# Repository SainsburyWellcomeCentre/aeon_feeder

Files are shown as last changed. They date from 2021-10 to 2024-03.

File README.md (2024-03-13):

# Aeon Feeder
Complete project repository for the underground feeder used in project Aeon.
## Folder Structure
### Code
This folder contains the VS Code project and code for the Raspberry Pi Pico
### eCAD
This folder contains 2 Altium Designer project folders for the Application Board and Beam Brake.

Within each project folder all the design files as well as another folder called __Project Outputs__

The __Project Outputs__ folder contains files for Documentation, Assembly and Fabrication.
### mCAD
This folder contains the complete mechanical design in Inventor 2023 project format.

To use this project within Inventor 2023+, the user should first open the Inventor Project file called **AEON.Feeder.ipj**

This will ensure Inventor is using the correct Project file to correctly find and assemble the the parts and assemblies within the Feeder.

The project can be opened from any location where the user has chosen to pull the whole project.

The main assembly for the complete model is **AEON.Feeder._Main.iam**

## Notes
The required software for the project is as follows
* Microsoft Visual Studio and Raspberry Pi Pico SDK as setup within the [Getting Started with Pico](https://datasheets.raspberrypi.com/pico/getting-started-with-pico.pdf)
* Altium Designer 23.5 or newer. Academic licenses can be obtained by contacting [Altium Education](https://www.altium.com/education/)
* Inventor Pro 2023 or newer. Academic licenses can be obtained by contacting [Autodesk Education](https://www.autodesk.com/education/home)

## Citation Policy

If you use this software or hardware, please cite it as below:

Sainsbury Wellcome Centre Foraging Behaviour Working Group. (2023). Aeon: An open-source platform to study the neural basis of ethological behaviours over naturalistic timescales,  https://doi.org/10.5281/zenodo.8411157



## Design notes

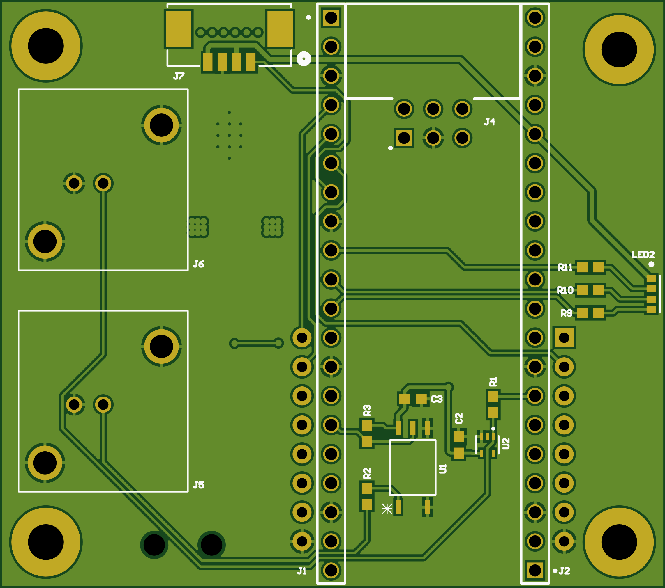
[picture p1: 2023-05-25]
mCAD/AEON.FeederElectronics/G_262400806_TopDecalImage.png

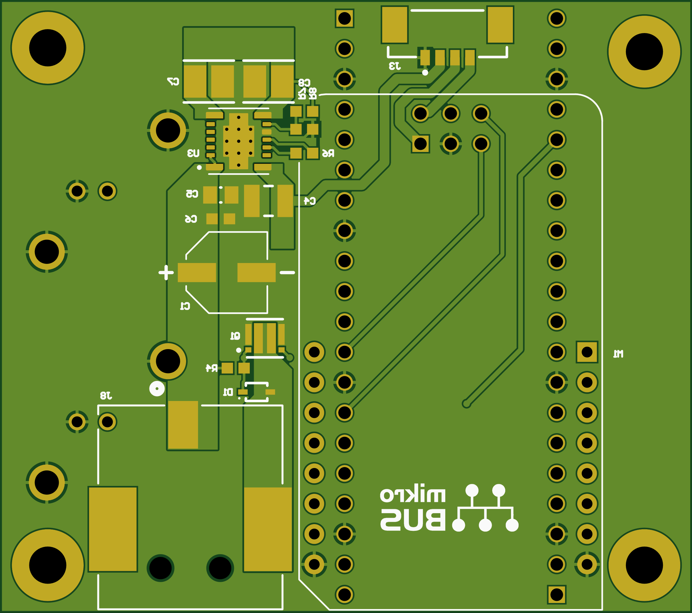
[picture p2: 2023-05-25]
mCAD/AEON.FeederElectronics/G_262400806_BottomDecalImage.png

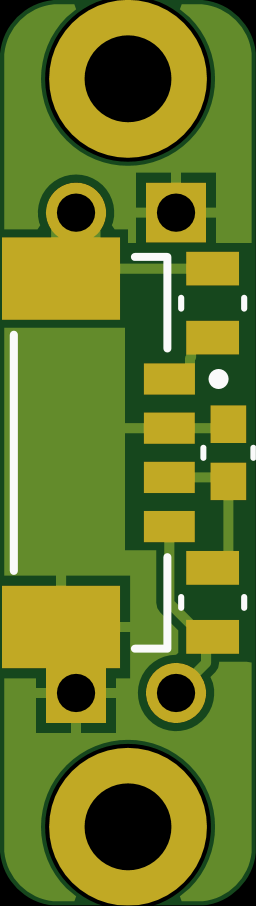
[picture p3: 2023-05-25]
mCAD/AEON.Feeder.BeamBreak/G_-1522103576_TopDecalImage.png

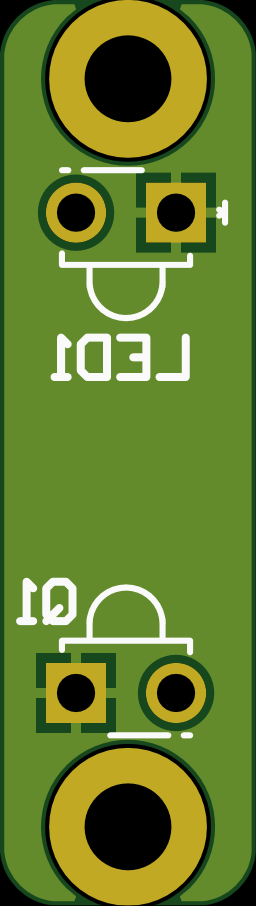
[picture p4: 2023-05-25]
mCAD/AEON.Feeder.BeamBreak/G_-1522103576_BottomDecalImage.png

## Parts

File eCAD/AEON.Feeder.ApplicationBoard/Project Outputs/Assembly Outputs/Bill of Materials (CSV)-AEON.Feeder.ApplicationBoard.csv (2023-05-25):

Comment | Description | Designator | Quantity
CPOLD-10uF-50V-20%-Alu | 10µF ±20% 50V SMD Aluminum Electrolytic Capacitor Surface Mount D | C1 | 1
C0603-100nF-100V-10%-X7R | 0.1µF ±10% 100V Ceramic Capacitor X7R 0603 (1608 Metric) | C2, C3, C6 | 3
C1210-10uF-50V-10%-X7R | 10uF ±10% 50V Ceramic Capacitor X7R 1210 (3225 Metric) | C4 | 1
C0805-1uF-50V-10%-X7R | 1uF ±10% 50V Ceramic Capacitor X7R 0805 (2012 Metric) | C5 | 1
C1210-47uF-10V-10%-X7R | 47uF ±10% 10V Ceramic Capacitor X7R 1210 (3225 Metric) | C7, C8 | 2
MM3Z10VB | DIODE ZENER 10V 200MW SOD323F | D1 | 1
SSW-120-01-x-S | Conn Socket Strip SKT 20 POS 2.54mm Solder ST Thru-Hole | J1 | 1
SSW-120-01-x-S - 21-40 | Conn Socket Strip SKT 20 POS 2.54mm Solder ST Thru-Hole (pins 21 - 40) | J2 | 1
53398-0471 | Board Connector, 4 Contact(s), 1 Row(s), Male, Straight, 0.049 inch Pitch, Surface Mount Terminal, Locking, Natural Insulator, Receptacle | J3 | 1
TST-103-04-x-D-RA | Board Connector, 6 Contact(s), 2 Row(s), Male, Right Angle, Solder Terminal | J4 | 1
1-1337541-0 | TE CONNECTIVITY / GREENPAR 1-1337541-0 RF / Coaxial Connector, BNC Coaxial, Straight Jack, Solder, 50 ohm, Brass | J5, J6 | 2
53261-0471 | MOLEX 1.25mm (.049") Pitch PicoBlade Header, Surface Mount, Right Angle, Lead-free, 4 Circuits | J7 | 1
694108105102 | DC Power Connectors WR-DC PwrJk CtrPnSMT Right Angled W/Peg | J8 | 1
MSL0601RGBU1 | Triple Color LED, Red/green/blue, Milky White | LED2 | 1
MIKROE-2699 | DRV8701 Brushed DC Motor Full-Bridge Gate DC Motor Driver 5 Click Add-On Board | M1 | 1
FDMC8030 | ON SEMICONDUCTOR - FDMC8030 - Dual MOSFET, Dual N Channel, 12 A, 40 V, 0.008 ohm, 10 V, 1.5 V | Q1 | 1
R0603-150R-1/16W-0.1% | Surface Mount Resistor 150 Ohm 1/16 W 0.1% 0603 (1608 Metric) | R1 | 1
R0603-270R-1/16W-0.1% | Surface Mount Resistor 270 Ohm 1/16 W 0.1% 0603 (1608 Metric) | R2 | 1
R0603-360R-1/16W-0.1% | Surface Mount Resistor 360 Ohm 1/16 W 0.1% 0603 (1608 Metric) | R3 | 1
R0603-2k7-1/16W-0.1% | Surface Mount Resistor 2k7 Ohm 1/16 W 0.1% 0603 (1608 Metric) | R4 | 1
R0603-100k-1/16W-0.1% | Surface Mount Resistor 100k Ohm 1/16 W 0.1% 0603 (1608 Metric) | R6 | 1
R0603-10k-1/16W-0.1% | Surface Mount Resistor 10k Ohm 1/16 W 0.1% 0603 (1608 Metric) | R7 | 1
R0603-2k49-1/16W-0.1% | Surface Mount Resistor 2.49k Ohm 1/16 W 0.1% 0603 (1608 Metric) | R8 | 1
R0603-1k5-1/16W-0.1% | Surface Mount Resistor 1k5 Ohm 1/16 W 0.1% 0603 (1608 Metric) | R9 | 1
R0603-560R-1/16W-0.1% | Surface Mount Resistor 560 Ohm 1/16 W 0.1% 0603 (1608 Metric) | R10 | 1
R0603-470R-1/16W-0.1% | Surface Mount Resistor 470 Ohm 1/16 W 0.1% 0603 (1608 Metric) | R11 | 1
TLP2368 | TOSHIBA TLP2368(E(O Digital Output Optocoupler, Open Collector, 1 Channel, SOIC, 5 Pins, 3.75 kV, 20 Mbaud | U1 | 1
TPD3E001DRLR | Low-Capacitance 3-Channel +/-15KV ESD-Protection Array for High-Speed Data Interfaces 5-SOT-5X3 | U2 | 1
TPSM5601R5HRDAR | 60-V input, 1-V to 16-V output, 1.5-A power module in enhanced HotRod™ QFN package 15-B3QFN -40 to 125 | U3 | 1

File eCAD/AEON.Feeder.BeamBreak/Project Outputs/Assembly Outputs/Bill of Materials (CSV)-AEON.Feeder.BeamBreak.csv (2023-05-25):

Comment | Description | Designator | Quantity
C0603-100nF-100V-10%-X7R | 0.1µF ±10% 100V Ceramic Capacitor X7R 0603 (1608 Metric) | C1 | 1
53398-0471 | Board Connector, 4 Contact(s), 1 Row(s), Male, Straight, 0.049 inch Pitch, Surface Mount Terminal, Locking, Natural Insulator, Receptacle | J1 | 1
GL480E00000F | EMITTER IR 950NM 50MA RADIAL | LED1 | 1
PT480FE0000F | SHARP PT480FE0000F PHOTOTRANSISTOR | Q1 | 1
RES 0805 200R 0.1% 125mW | RES 0805 200 Ohm 0.1% 1/8W ±10ppm/°C Thin Film | R1 | 1
R0603-6k8-1/16W-0.1% | Surface Mount Resistor 6.8k Ohm 1/16 W 0.1% 0603 (1608 Metric) | R2 | 1

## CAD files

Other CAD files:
mCAD/AEON.AcrylicTop.ipt
mCAD/AEON.AluminiumFrame.ipt
mCAD/AEON.Feeder.Base.ipt
mCAD/AEON.Feeder.BeamBreak/ConvertedComponents/FP-533980471-MFG_CMP-370-0030-2.ipt
mCAD/AEON.Feeder.BeamBreak/ConvertedComponents/FP-GRM188-0_1-e0_2_0_5-IPC_B_CMP-611-0027-15.ipt
mCAD/AEON.Feeder.BeamBreak/ConvertedComponents/GL480_5.8mm_CMP-520-0009-4.ipt
mCAD/AEON.Feeder.BeamBreak/ConvertedComponents/PT480_5.8_CMP-500-0000-3.ipt
mCAD/AEON.Feeder.BeamBreak/ConvertedComponents/RES_ERA6A_0805_PAN_CMP-633-0035-1.ipt
mCAD/AEON.Feeder.BeamBreak/ConvertedComponents/RES_ERA6A_0805_PAN_CMP-633-0036-1.ipt
mCAD/AEON.Feeder.BeamBreak/ND.ForageFeeder.BeamBreak.iam
mCAD/AEON.Feeder.BeamBreak/ND.ForageFeeder.BeamBreak_BOARD.ipt
mCAD/AEON.Feeder.BeamBreakBlock.ipt
mCAD/AEON.Feeder.BearingSpacer.ipt
mCAD/AEON.Feeder.ClampBlock.ipt
mCAD/AEON.Feeder.ClampUpper.ipt
mCAD/AEON.Feeder.Disc.ipt
mCAD/AEON.Feeder.EncodeMount.ipt
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

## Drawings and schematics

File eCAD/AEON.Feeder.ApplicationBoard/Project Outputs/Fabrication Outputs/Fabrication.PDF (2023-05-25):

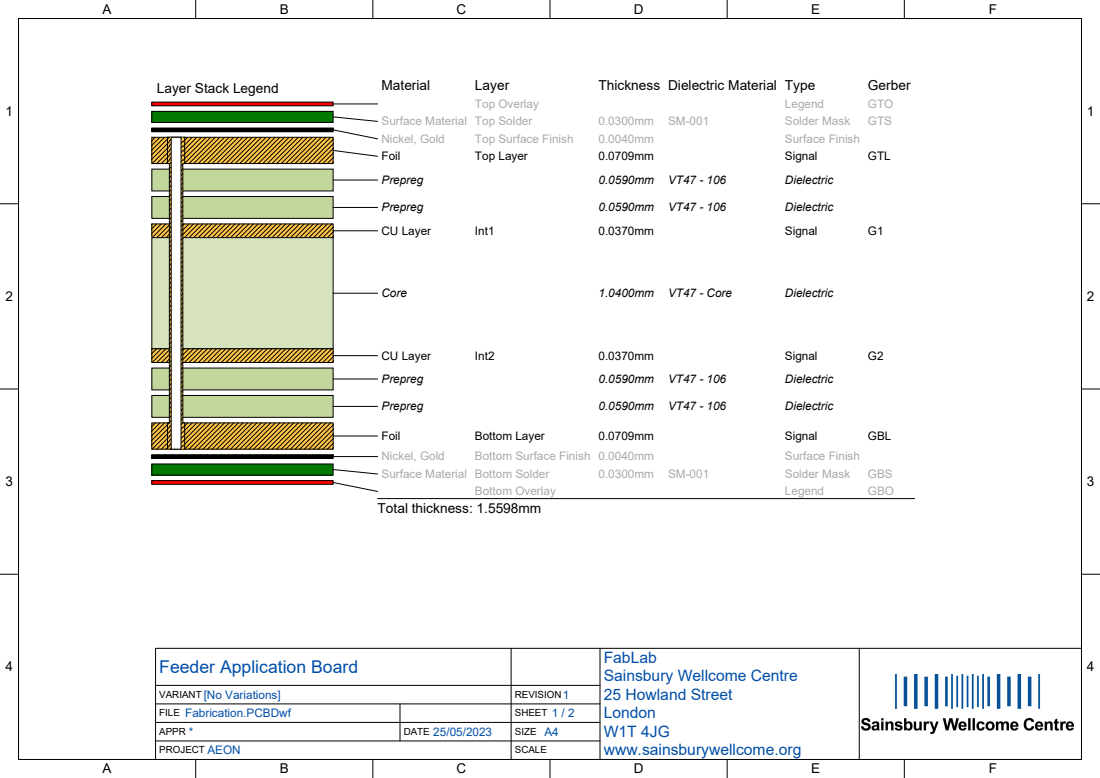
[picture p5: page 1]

[No Variations] VARIANT | 1 REVISION
FILE Fabrication.PCBDwf | | SHEET 1 / 2
APPR * | DATE 25/05/2023 | SIZE A4

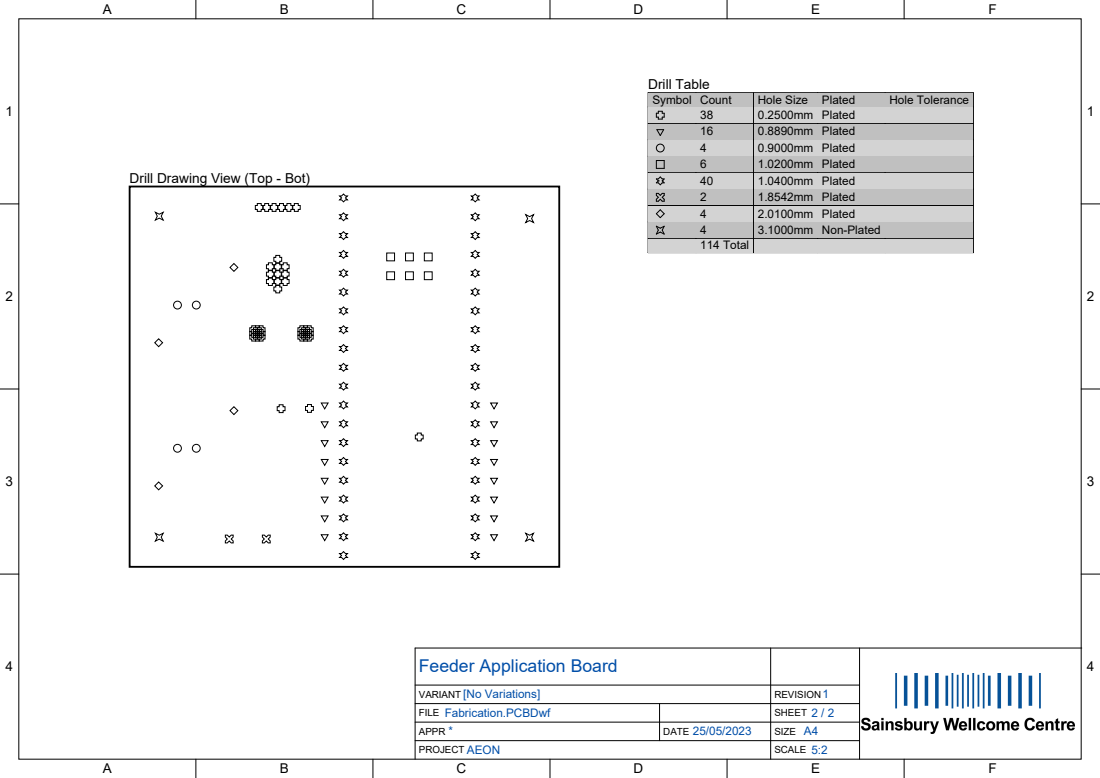
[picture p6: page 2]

Symbol | Count | Hole Size | Plated | Hole Tolerance

38 | 0.2500mm | Plated
16 | 0.8890mm | Plated
4 | 0.9000mm | Plated
6 | 1.0200mm | Plated
40 | 1.0400mm | Plated
2 | 1.8542mm | Plated
4 | 2.0100mm | Plated
4 | 3.1000mm | Non-Plated
114 Total

Drill Drawing View (Top - Bot)

[No Variations] VARIANT | 1 REVISION
FILE Fabrication.PCBDwf | | SHEET 2 / 2
APPR * | DATE 25/05/2023 | SIZE A4

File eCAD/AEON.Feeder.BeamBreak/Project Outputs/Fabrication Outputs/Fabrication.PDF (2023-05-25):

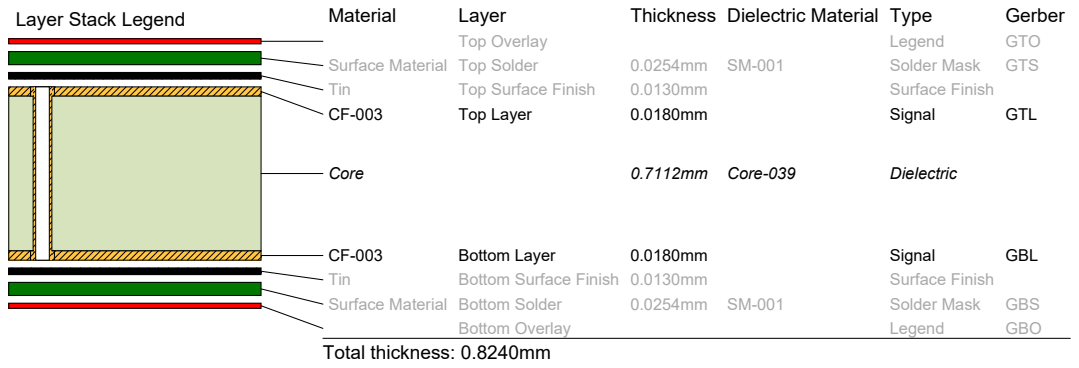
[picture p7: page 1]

[No Variations] VARIANT | 1 REVISION
FILE Fabrication.PCBDwf | | SHEET 1 / 2
APPR * | DATE 25/05/2023 | SIZE A4

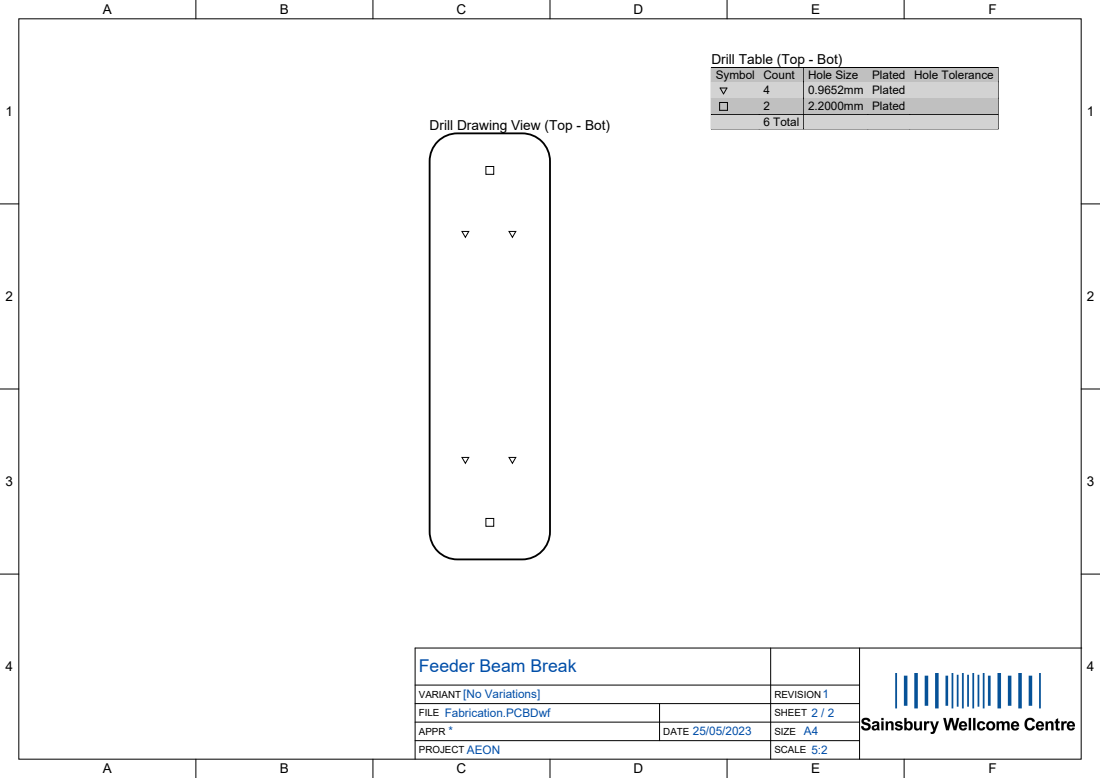
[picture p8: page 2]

Drill Table (Top - Bot)

Symbol | Count | Hole Size | Plated | Hole Tolerance

4 | 0.9652mm | Plated
2 | 2.2000mm | Plated
6 Total

Drill Drawing View (Top - Bot)

[No Variations] VARIANT | 1 REVISION
FILE Fabrication.PCBDwf | | SHEET 2 / 2
APPR * | DATE 25/05/2023 | SIZE A4

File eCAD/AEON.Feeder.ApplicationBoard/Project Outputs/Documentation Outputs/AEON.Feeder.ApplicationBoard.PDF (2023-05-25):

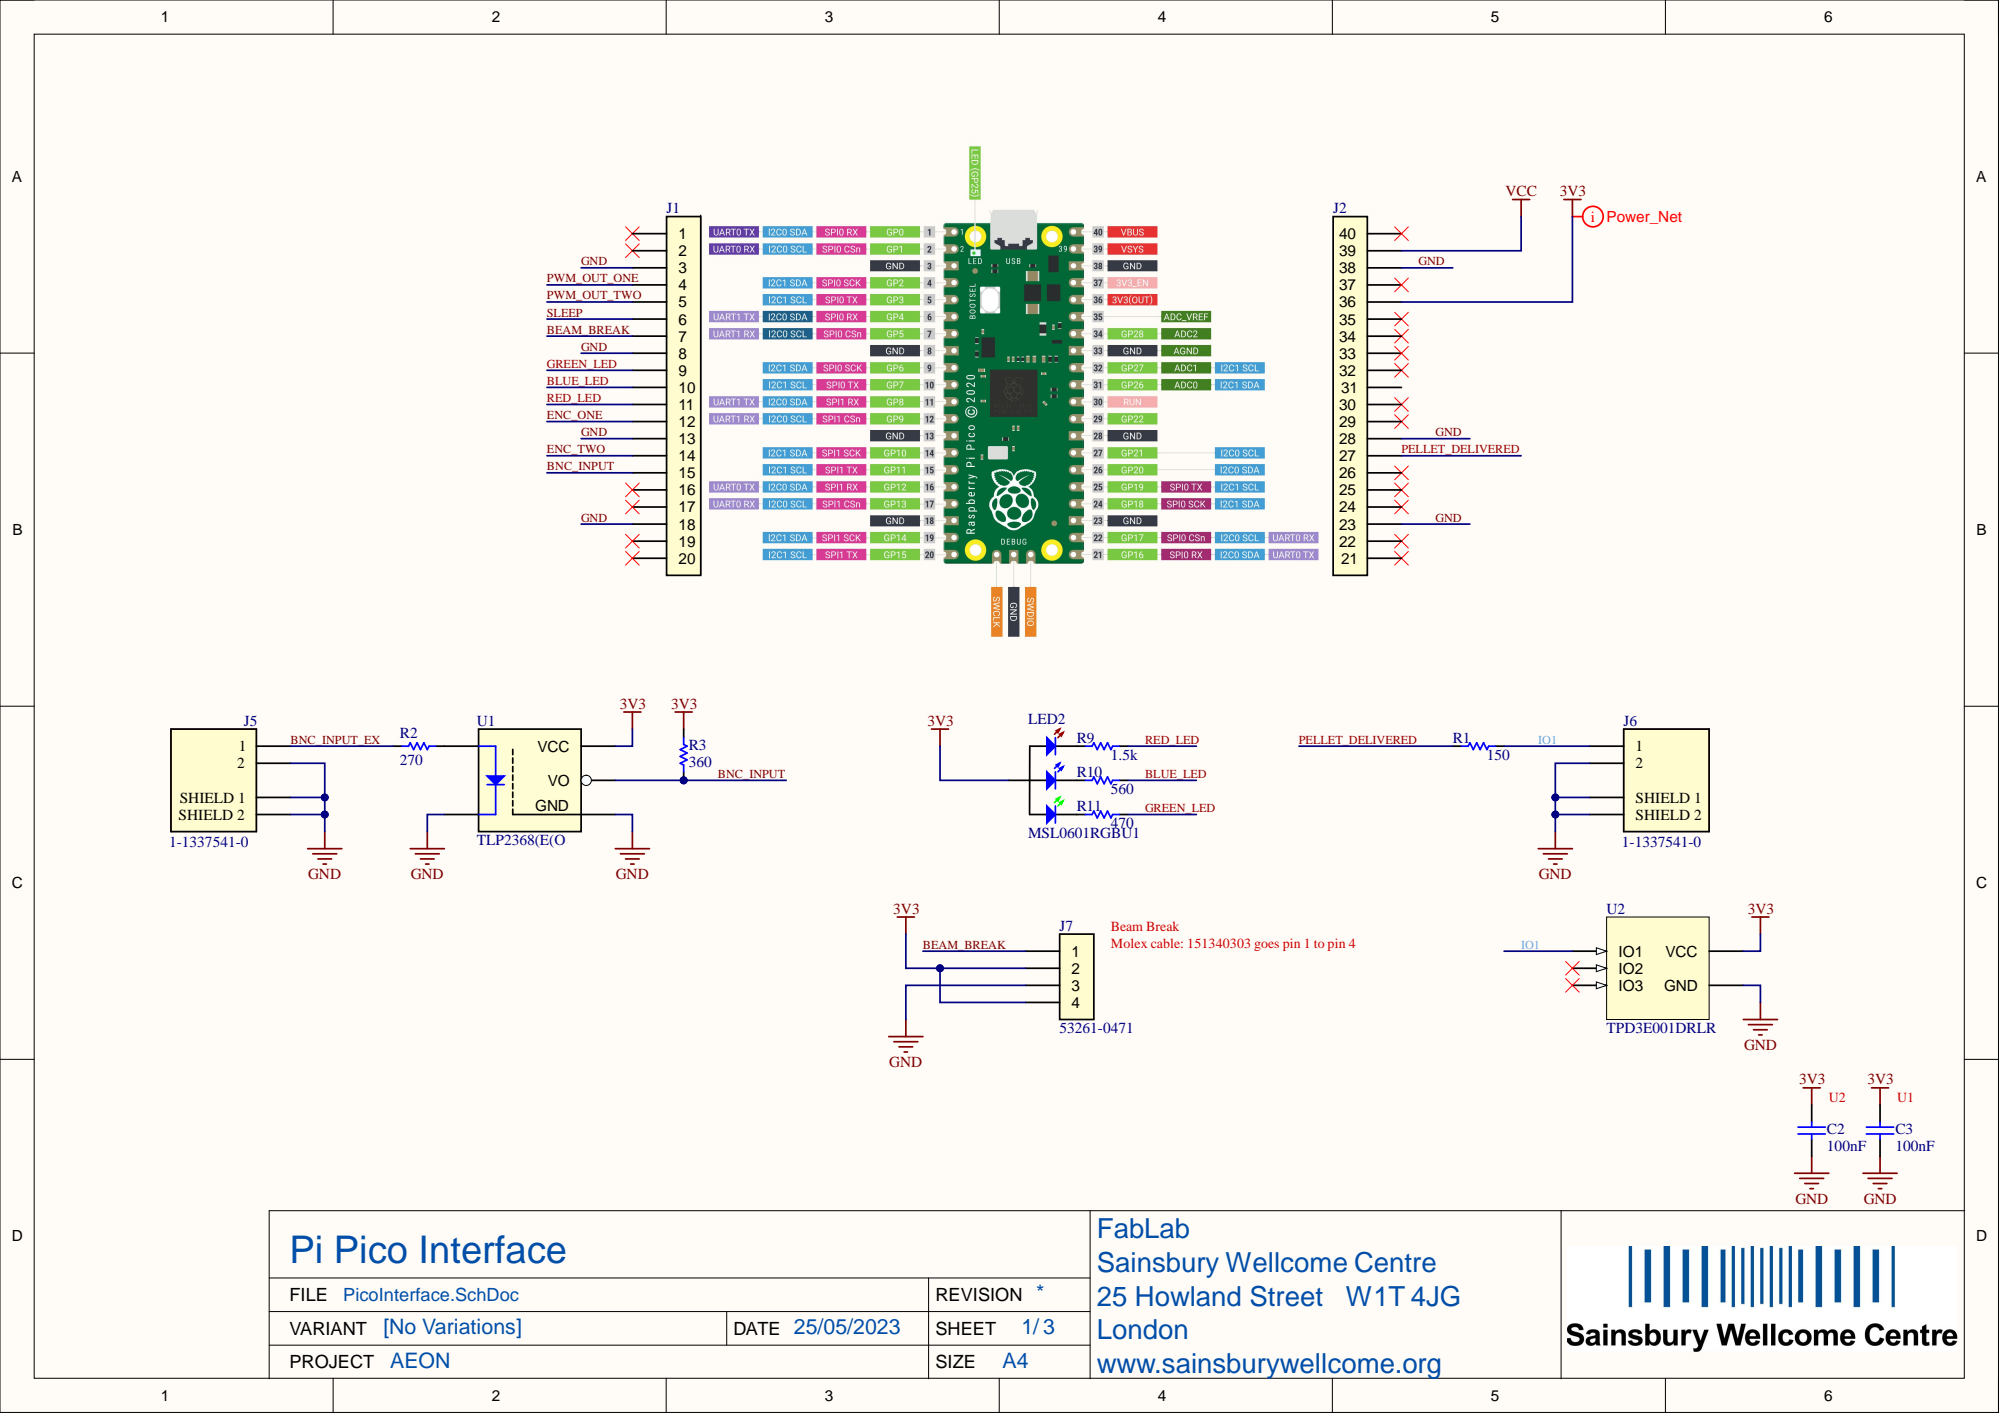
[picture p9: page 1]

Beam Break
Molex cable: 151340303 goes pin 1 to pin 4

FILE PicoInterface.SchDoc | * REVISION

VARIANT [No Variations] | DATE | SHEET /

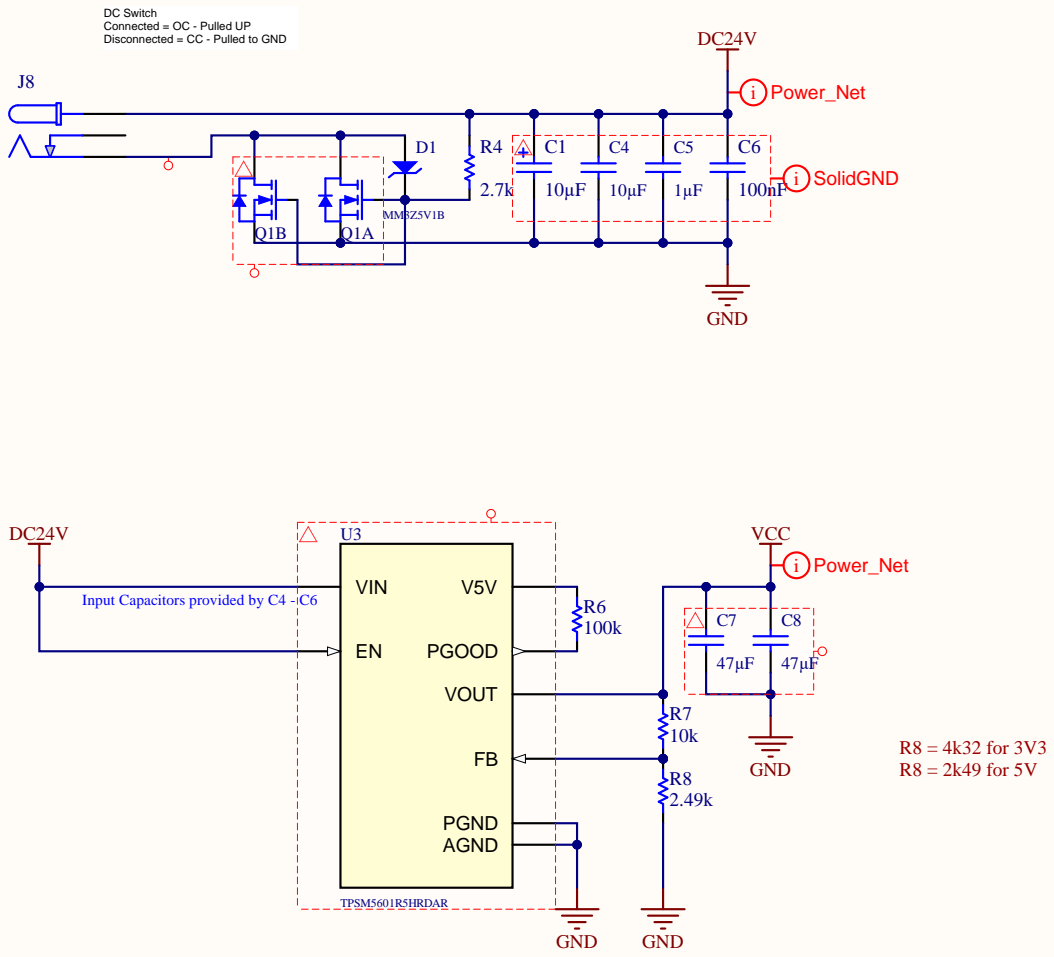
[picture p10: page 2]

DC Switch
Connected = OC - Pulled UP
Disconnected = CC - Pulled to GND

Input Capacitors provided by C4 - C6

PowerSupply.SchDoc | *

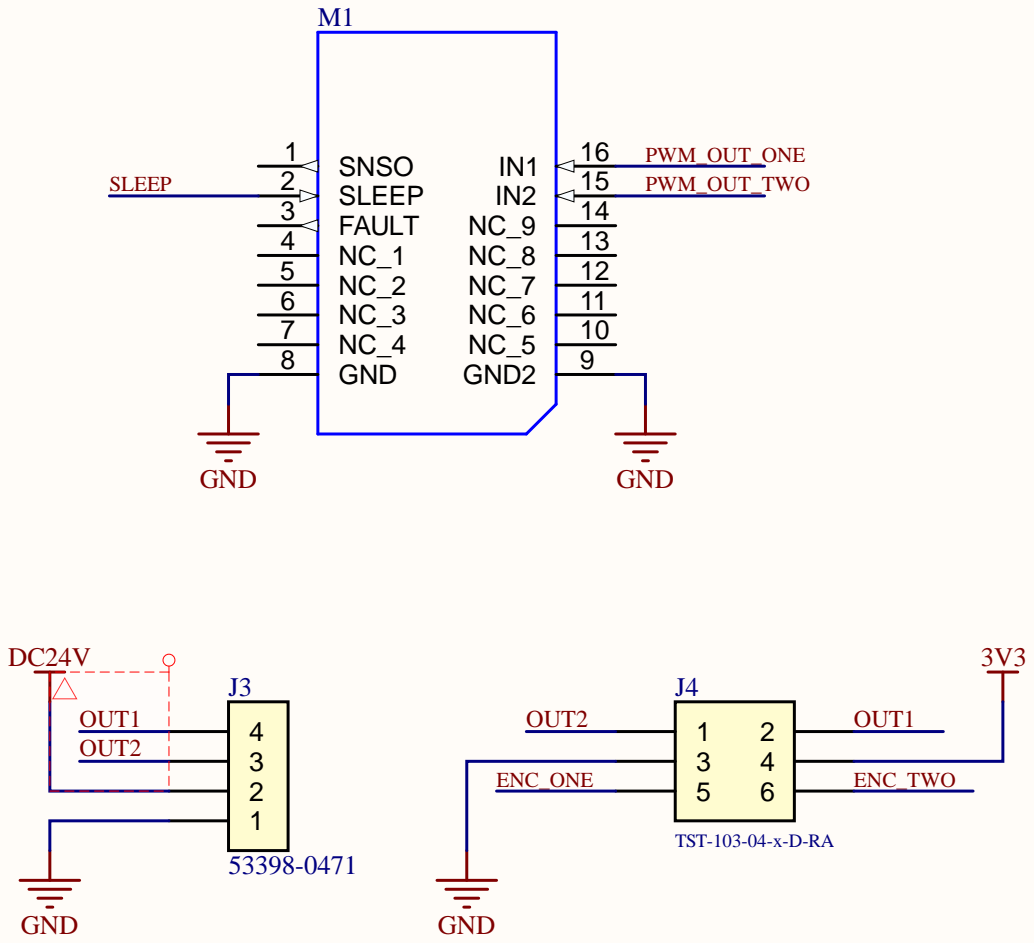
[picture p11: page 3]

Mikroe Motor Click 5 interface

MotorDriver.Mikroe.SchDoc | 1

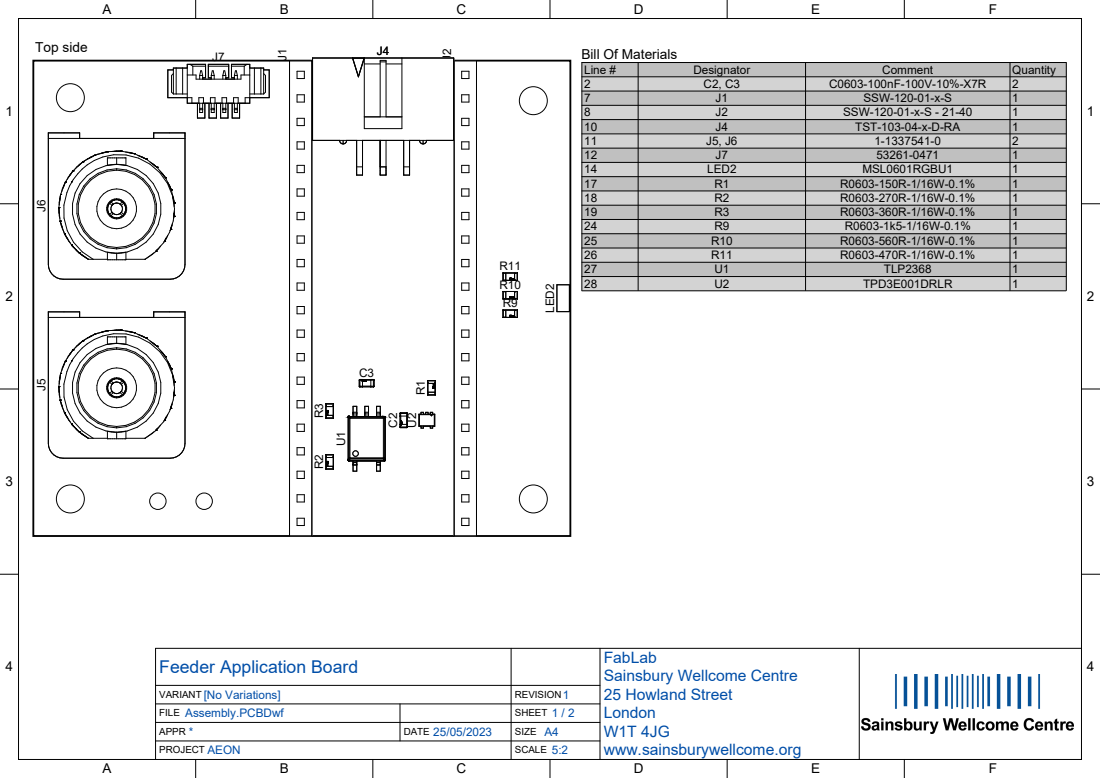
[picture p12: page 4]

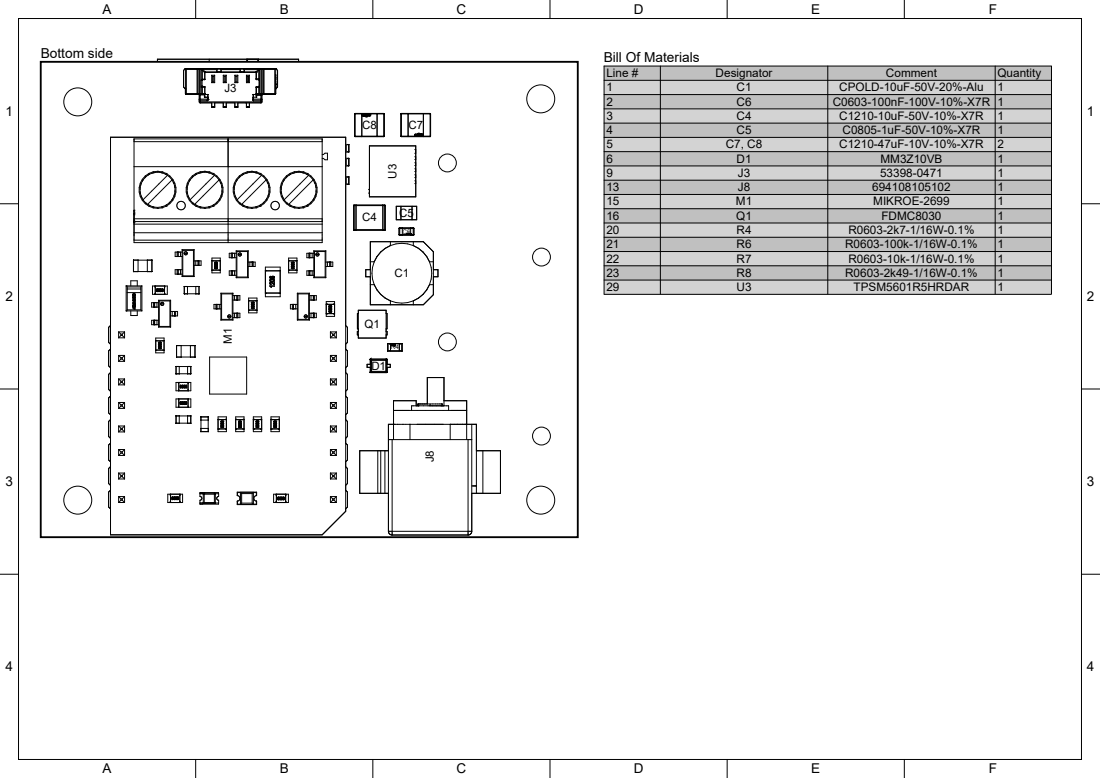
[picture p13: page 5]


[No Variations] VARIANT | 1 REVISION
FILE Fabrication.PCBDwf | | SHEET 1 / 2


Symbol | Count | Hole Size | Plated | Hole Tolerance

38 | 0.2500mm | Plated
16 | 0.8890mm | Plated
4 | 0.9000mm | Plated
6 | 1.0200mm | Plated
40 | 1.0400mm | Plated
2 | 1.8542mm | Plated
4 | 2.0100mm | Plated
4 | 3.1000mm | Non-Plated
114 Total

Drill Drawing View (Top - Bot)

[No Variations] VARIANT | 1 REVISION
FILE Fabrication.PCBDwf | | SHEET 2 / 2

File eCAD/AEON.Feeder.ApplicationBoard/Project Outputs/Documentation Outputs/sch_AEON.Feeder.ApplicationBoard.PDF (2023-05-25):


Beam Break
Molex cable: 151340303 goes pin 1 to pin 4

FILE PicoInterface.SchDoc | * REVISION

VARIANT [No Variations] | DATE | SHEET /


DC Switch
Connected = OC - Pulled UP
Disconnected = CC - Pulled to GND

Input Capacitors provided by C4 - C6

PowerSupply.SchDoc | *


Mikroe Motor Click 5 interface

MotorDriver.Mikroe.SchDoc | 1

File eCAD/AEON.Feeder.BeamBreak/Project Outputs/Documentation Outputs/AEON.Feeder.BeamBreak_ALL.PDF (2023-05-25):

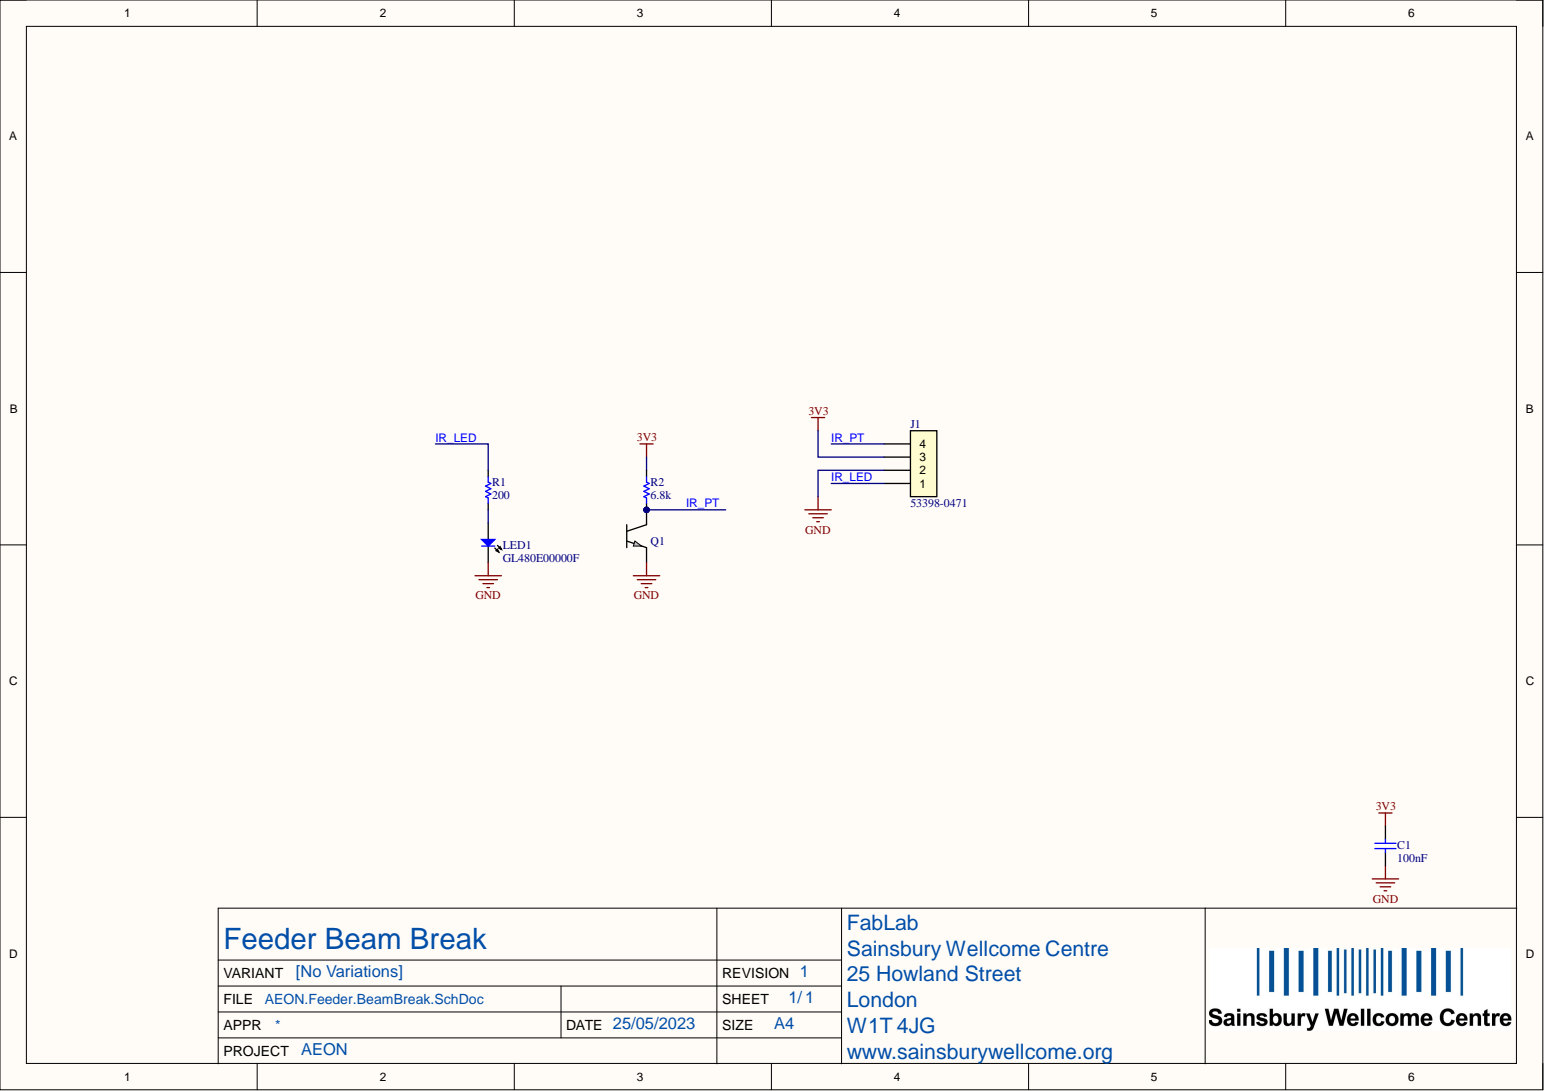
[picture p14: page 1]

PROJECT AEON VARIANT [No Variations] FILE AEON.Feeder.BeamBreak.SchDoc | | 1 / 1 SHEET

1 REVISION

APPR * | DATE 25/05/2023 | SIZE A4

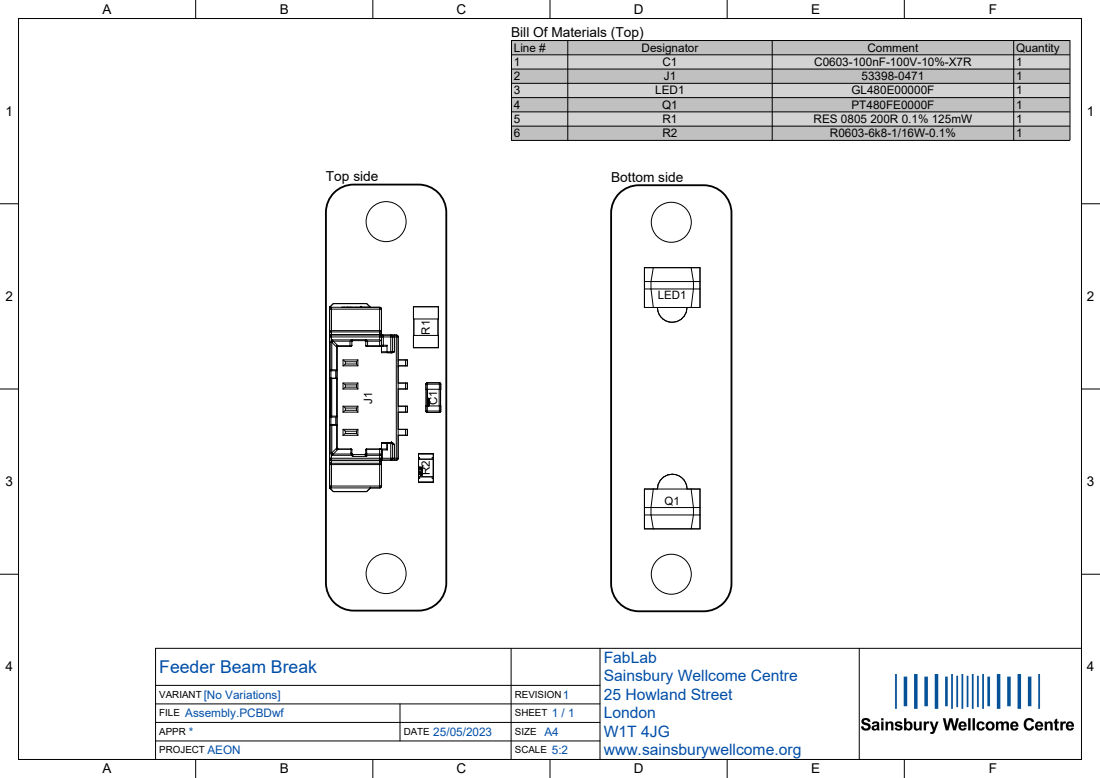
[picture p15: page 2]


[No Variations] VARIANT | 1 REVISION
FILE Fabrication.PCBDwf | | SHEET 1 / 2


Drill Table (Top - Bot)

Symbol | Count | Hole Size | Plated | Hole Tolerance

4 | 0.9652mm | Plated
2 | 2.2000mm | Plated
6 Total

Drill Drawing View (Top - Bot)

[No Variations] VARIANT | 1 REVISION
FILE Fabrication.PCBDwf | | SHEET 2 / 2




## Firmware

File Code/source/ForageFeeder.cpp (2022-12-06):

#include <math.h>
#include <vector>
#include <string.h>
// #include <cstdlib>
#include <stdio.h>
#include "pico/stdlib.h"
#include "pico/multicore.h"
#include "hardware/pio.h"
#include "hardware/gpio.h"
#include "pico/time.h"
#include "hardware/irq.h"
#include "hardware/timer.h"
#include "hardware/divider.h"
#include "hardware/pwm.h"
#include "FreeRTOS.h"
#include "task.h"

#include <tusb.h>
#include "pico/unique_id.h"

#include "pid.h"
// #include "pio_quad_encoder.pio.h"
#include "pio_quad_encoder.h"

////////////////////////////////////////
// Define Code Switches
////////////////////////////////////////
#define WAIT_USB            1       // set to 0 disable waiting for USB
#define UART_DEBUG          1

////////////////////////////////////////
// Define Hardware Pins
////////////////////////////////////////
#define PWM_OUT_ONE_PIN         2
#define PWM_OUT_TWO_PIN         3
#define PWM_EN_PIN              4
#define BEAM_BREAK_PIN          5
#define GREEN_RGB_LED_PIN       6
#define BLUE_RGB_LED_PIN        7
#define RED_RGB_LED_PIN         8
#define ENC_ONE_PIN             9
#define ENC_TWO_PIN             10
#define BNC_INPUT_PIN           11
#define PELLET_DELIVERED_PIN    21
#define GREEN_LED_PIN           25

////////////////////////////////////////
// Define SET Software Values
////////////////////////////////////////
#define GPIO_ON             1
#define GPIO_OFF            0

#define RGB_ON              0
#define RGB_OFF             1

#define LEVEL_LOW           0x1
#define LEVEL_HIGH          0x2
#define EDGE_FALL           0x4
#define EDGE_RISE           0x8

// for 24 hole feeder disk
#define TIME_DIF_MAX        1000u
#define MAX_ROTATION_TOTAL  23104u
#define MAX_ROTATION_HOLE   963u    // 1925u basically MAX_ROTATION_TOTAL / 12 (number of holes) --- for 24 holes 963u
#define ROTATION_PRE_LOAD   800u   // distance to travel around before stopping from the last hole to pre load a pellet was 1500u for 12 hole and 500u for 24 (initially)
#define ROTATION_OVERSHOOT  250u    // How far to overshoot the front of the hole - gives the pellet more time to drop before a false negative is picked up.
#define SPEED_MAX           400u
#define SPEED_PRE_LOAD      300u
#define SPEED_DELIVER       400u
#define POSITION_MARGIN     15u


// #define SPEED_MAX           100u
// #define SPEED_PRE_LOAD      50u
// #define SPEED_DELIVER       100u

#define USB_WAIT_TIME           100u     // 10 seconds (100 * 0.1ms)
#define UART_STRING_BUF_SIZE    40

#define MULTICORE_FIFO_TIMEOUT  1000u

#define BNC_TRIGGER_TIME_LIMIT      20u     // upper limit of 20 ms (more likely 1ms)
#define BNC_INITIALISE_TIME_LIMIT   25u     // low limit of 25ms

#define MAX_INITIALISE_COUNT    12u          // was 6 originally but increased to 12

////////////////////////////////////////
// Define Feeder Application States
////////////////////////////////////////

#define FEEDER_INITIALISE           0x01
#define FEEDER_PRE_LOAD             0x02
#define FEEDER_DELIVERED            0x04
#define FEEDER_DELIVERY_ERROR       0x08

////////////////////////////////////////
// Define Display Update Types
////////////////////////////////////////

#define DISPLAY_MESSAGE             0x01
#define DISPLAY_STATUS              0x02
#define DISPLAY_COUNTS              0x04

////////////////////////////////////////
// Velocity Controller parameters
////////////////////////////////////////
#define PID_VEL_KP  10.0f
#define PID_VEL_KI  20.0f
#define PID_VEL_KD  0.002f

#define PID_VEL_TAU 0.200f

#define PID_VEL_LIM_MIN -4095.0f
#define PID_VEL_LIM_MAX  4095.0f

#define PID_VEL_LIM_MIN_INT -4095.0f
#define PID_VEL_LIM_MAX_INT  4095.0f

#define SAMPLE_TIME_VEL_S 0.002f

////////////////////////////////////////
// Position Controller parameters
////////////////////////////////////////
#define PID_POS_KP  0.3f
#define PID_POS_KI  0.08f
#define PID_POS_KD  0.005f

#define PID_POS_TAU 0.02f

#define PID_POS_LIM_MIN -400.0f
#define PID_POS_LIM_MAX  400.0f

#define PID_POS_LIM_MIN_INT -25.0f
#define PID_POS_LIM_MAX_INT  25.0f

#define SAMPLE_TIME_POS_S 0.002f

////////////////////////////////////////
// Define classes / structs / ints etc.
////////////////////////////////////////

QuadEncoder quad_encoder(ENC_ONE_PIN);

PIDController pid_vel = { PID_VEL_KP, PID_VEL_KI, PID_VEL_KD,
                        PID_VEL_TAU,
                        PID_VEL_LIM_MIN, PID_VEL_LIM_MAX,
                        PID_VEL_LIM_MIN_INT, PID_VEL_LIM_MAX_INT,
                        SAMPLE_TIME_VEL_S };

PIDController pid_pos = { PID_POS_KP, PID_POS_KI, PID_POS_KD,
                        PID_POS_TAU,
                        PID_POS_LIM_MIN, PID_POS_LIM_MAX,
                        PID_POS_LIM_MIN_INT, PID_POS_LIM_MAX_INT,
                        SAMPLE_TIME_POS_S };

struct repeating_timer control_loop;

// Debounce control
// unsigned long time = to_ms_since_boot(get_absolute_time());
// const int delayTime =  250;
// block extra pellet triggers per shot - to fix pellet count
// unsigned long pellet_time = to_ms_since_boot(get_absolute_time());

unsigned long bnc_trigger_rise_time;
unsigned long bnc_trigger_fall_time;
// const int pellet_delay_time =  50;         // was 250ms but was missing pellets when fine tuning speed of delivery

volatile int32_t motor_position = 0;
volatile int32_t motor_position_buf;
volatile int32_t motor_position_old = 0;
volatile int32_t position_setpoint = 0;   // Feeder Position setpoint
volatile int32_t motor_speed = 0;           // Actual measued speed from the motor
volatile int32_t motor_speed_buf; 
volatile int32_t speed_setpoint = 0;   // Motor Speed setpoint
volatile int32_t speed_pid_out = 0;   // Motor Speed setpoint
volatile int32_t speed_limit = 0;   // Motor Speed setpoint
uint16_t set_pwm_one = 0;               // PWM values for writing to Timer
uint16_t set_pwm_two = 0;               // PWM values for writing to Timer
static bool motor_moving;             // Flag to update screens etc.
static bool feeder_position_reached;  // flag to set when the feeder has reached the position setpoint (within a margin set by POSITION_MARGIN)

static bool pellet_delivered = false;         // Flag set when pellet gets delivered
static bool pellet_delivered_int = false;         // Flag set when pellet gets delivered
static bool pellet_delivered_led = false;
volatile int32_t pellet_delivered_count_1 = 0;
volatile int32_t pellet_delivered_count_2 = 0;
volatile int32_t pellet_delivered_count_3 = 0;
volatile int32_t pellet_delivered_count_4 = 0;
volatile int32_t pellet_delivered_count_5 = 0;
volatile int32_t pellet_delivered_count_6 = 0;
volatile int32_t pellet_delivered_msg_count = 0;
static bool missed_pellet;
volatile bool uart_message_flag;
volatile bool motor_brake;
volatile bool bnc_triggered;
volatile bool led_toggle;
volatile bool h_bridge_start;

volatile bool A_flag;
volatile bool B_flag;
volatile bool X_flag;
volatile bool Y_flag;

volatile uint32_t application_status = 0;
volatile uint32_t application_flags = 0;

divmod_result_t delta_time_hw;
divmod_result_t motor_speed_hw;

// static char event_str[128];

static char uart_message_str[UART_STRING_BUF_SIZE];

// Define FreeRTOS Task
void vSerialDebugTask( void * pvParameters );
void vApplicationTask( void * pvParameters );
void vSystemMonitorTask( void * pvParameters );

bool feeder_initialise(int attempt);
bool feeder_pre_load_pellet(void);
bool feeder_deliver_pellet(void);
bool feeder_deliver_error(void);

// void gpio_event_string(char *buf, uint32_t events);

////////////////////////////////////////
// Interupt Callback Routines - START
////////////////////////////////////////
// CORE 1 - START
////////////////////////////////////////
// GPIO Interupt
void gpio_callback_core_1(uint gpio, uint32_t events) {
    // irq_clear(IO_IRQ_BANK0);
}

////////////////////////////////////////
// CORE 1 - END
////////////////////////////////////////

////////////////////////////////////////
// CORE 0 - START
////////////////////////////////////////
// Alarm callbacks

int64_t green_led_callback(alarm_id_t id, void *user_data) {
    gpio_put(GREEN_RGB_LED_PIN, RGB_OFF);
    gpio_put(RED_RGB_LED_PIN, RGB_ON);
    return 0;
}

int64_t amber_led_callback(alarm_id_t id, void *user_data) {
    gpio_put(GREEN_LED_PIN, GPIO_OFF);
    if (pellet_delivered_led) {
        add_alarm_in_ms(200, green_led_callback, NULL, false);
        gpio_put(RED_RGB_LED_PIN, RGB_OFF);
        pellet_delivered_led = false;
    } else {
        gpio_put(GREEN_RGB_LED_PIN, RGB_OFF);
    }
    return 0;
}
// GPIO Interupt
void gpio_callback_core_0(uint gpio, uint32_t events) {

    switch(gpio) {
        case BEAM_BREAK_PIN:
            switch (events) {   
                case EDGE_RISE:
                    gpio_put(PELLET_DELIVERED_PIN, GPIO_ON);
                    pellet_delivered = true;
                    pellet_delivered_led = true;
                    pellet_delivered_int = true;
                    break;          
                case EDGE_FALL:
                    gpio_put(PELLET_DELIVERED_PIN, GPIO_OFF);
                    break;
                default:
                    break;
            }
            break;
        case BNC_INPUT_PIN:
            switch (events) {
                case EDGE_FALL:      // Lab Unit
                // case EDGE_RISE:         // Bench Prototype
                    bnc_trigger_fall_time = to_ms_since_boot(get_absolute_time());
                    // gpio_put(GREEN_LED_PIN, GPIO_ON);
                    break;
                case EDGE_RISE:      // Lab Unit
                // case EDGE_FALL:         // Bench Prototype
                    bnc_trigger_rise_time = to_ms_since_boot(get_absolute_time());
                    // gpio_put(GREEN_LED_PIN, GPIO_OFF);
                    if ((bnc_trigger_rise_time - bnc_trigger_fall_time) > BNC_INITIALISE_TIME_LIMIT) {
                        application_status = FEEDER_INITIALISE;
                        application_flags = 0;
                        A_flag = true;
                        // gpio_put(GREEN_LED_PIN, GPIO_ON);
                    } else if ((bnc_trigger_rise_time - bnc_trigger_fall_time) < BNC_TRIGGER_TIME_LIMIT) {
                        bnc_triggered = true;
                        add_alarm_in_ms(200, amber_led_callback, NULL, false);
                        gpio_put(GREEN_RGB_LED_PIN, RGB_ON);
                        gpio_put(GREEN_LED_PIN, GPIO_ON);
                    }
                    break;
                default:
                    break;
            }           
            break;
        default:
            break;
    }

}
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

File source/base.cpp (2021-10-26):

#include <math.h>
#include <vector>
// #include <string.h>
// #include <cstdlib>

// #include <stdio.h>
#include "pico/stdlib.h"
#include "pico/multicore.h"
#include "hardware/gpio.h"
#include "pico/time.h"
#include "hardware/irq.h"
#include "hardware/pwm.h"
#include "FreeRTOS.h"
#include "task.h"

#include "breakout_colourlcd240x240.hpp"

#include "gfxfont.h"
#include "FreeMono12pt7b.h"
#include "FreeSansBoldOblique12pt7b.h"
#include "FreeSerif24pt7b.h"


// Screen demo switches
#define SCREEN_TEXT         1

#define ROTARY_SW           7
#define ROTARY_A            8
#define ROTARY_B            9
#define PWM_IN_ONE          10
#define PWN_IN_TWO          11
#define ENC_ONE             12
#define ENC_TWO             13
#define PWM_EN              14
#define GREEN_LED_PIN       25

#define GPIO_ON             1
#define GPIO_OFF            0

using namespace pimoroni;

uint16_t buffer[BreakoutColourLCD240x240::WIDTH * BreakoutColourLCD240x240::HEIGHT];
BreakoutColourLCD240x240 lcd(buffer);


static char event_str[128];

char lcd_message_str[20];

void gpio_event_string(char *buf, uint32_t events);


// Interupt Callback Routines - START
void gpio_callback_rotary_sw(uint gpio, uint32_t events) {
    // Put the GPIO event(s) that just happened into event_str
    // so we can print it
    gpio_event_string(event_str, events);
    sprintf(lcd_message_str, "GPIO %d %s\n", gpio, event_str);
    printf("GPIO %d %s\n", gpio, event_str);
}

void gpio_callback_rotary(uint gpio, uint32_t events) {
    // Put the GPIO event(s) that just happened into event_str
    // so we can print it
    gpio_event_string(event_str, events);
    sprintf(lcd_message_str, "GPIO %d %s\n", gpio, event_str);
    printf("GPIO %d %s\n", gpio, event_str);
}

void gpio_callback_motor(uint gpio, uint32_t events) {
    // Put the GPIO event(s) that just happened into event_str
    // so we can print it
    gpio_event_string(event_str, events);
    // sprintf(lcd_message_str, "GPIO %d %s\n", gpio, event_str);
    printf("GPIO %d %s\n", gpio, event_str);
}

void on_pwm_wrap_one() {
    // static int fade = 0;
    // static bool going_up = true;
    // Clear the interrupt flag that brought us here
    pwm_clear_irq(pwm_gpio_to_slice_num(PWM_IN_ONE));

    // if (going_up) {
    //     ++fade;
    //     if (fade > 255) {
    //         fade = 255;
    //         going_up = false;
    //     }
    // } else {
    //     --fade;
    //     if (fade < 0) {
    //         fade = 0;
    //         going_up = true;
    //     }
    // }
    // Square the fade value to make the LED's brightness appear more linear
    // Note this range matches with the wrap value
    // pwm_set_gpio_level(PWM_IN_ONE, fade * fade);
    pwm_set_gpio_level(PWM_IN_ONE, 2058);
}

// Interupt Callback Routines - END

// Define FreeRTOS Task
void vGreenLEDTask( void * pvParameters );

static const char *gpio_irq_str[] = {
        "LEVEL_LOW",  // 0x1
        "LEVEL_HIGH", // 0x2
        "EDGE_FALL",  // 0x4
        "EDGE_RISE"   // 0x8
};

// SWC Base code - will run on Core 1 - START
void swc_base() {
  
    printf("Hello GPIO IRQ\n");
    sprintf(lcd_message_str, "Hello GPIO IRQ");
    gpio_set_irq_enabled_with_callback(ROTARY_SW, GPIO_IRQ_EDGE_RISE | GPIO_IRQ_EDGE_FALL, true, &gpio_callback_rotary_sw);
    gpio_set_irq_enabled_with_callback(ROTARY_A, GPIO_IRQ_EDGE_FALL, true, &gpio_callback_rotary);
    gpio_set_irq_enabled_with_callback(ROTARY_B, GPIO_IRQ_EDGE_FALL, true, &gpio_callback_rotary);

    lcd.init();
    lcd.set_backlight(255);

  while(true) {
    lcd.set_pen(120, 40, 60);
    lcd.clear();

#if SCREEN_TEXT
    lcd.set_pen(255,255,255);
    lcd.customFontSetFont((const pimoroni::GFXfont&)FreeSansBoldOblique12pt7b);
    // lcd.customFontSetFont((const pimoroni::GFXfont&)FreeMono12pt7b);
    // lcd.customFontSetFont((const pimoroni::GFXfont&)FreeSerif24pt7b); 
    // lcd.customFontSetFont();
    // sprintf(lcd_message_str, "Hello");
    lcd.text(lcd_message_str, Point(0, 30), 240, 1);  
    // lcd.text("Wellcome", Point(0, 30), 240, 1); 

#endif
    // update screen
    lcd.update();
    }
}
// SWC Base code - will run on Core 1 - END
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

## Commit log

2021-11-12 clean up code and added motor breaking
2021-11-18 Clean up feeder case code - seems to be working properly now
2021-11-22 Added GPIO pin outs for Pellet delivered and Feeder Error
2022-04-08 BNC rising edge 12 hole disk
2022-05-13 Added RGB LED code
2023-05-25 Added mCAD files
    [2619S_SR_IE2-16.ipt, 5pin_SO6_TOS_CMP-530-0000-11.ipt, AEON.AcrylicTop.ipt, AEON.AluminiumFrame.ipt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]
2023-05-25 checking mCAD after merge
    [AEON.Feeder._Main.iam, ND.ForageFeeder.BeamBreak.iam, ND.ForageFeeder.BeamBreak_BOARD.ipt, ND.ForagingFeeder.Electronics.iam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]
2023-05-25 Added eCAD files
    [AEON.Feeder.ApplicationBoard.PcbDoc, AEON.Feeder.ApplicationBoard.PrjPcb, AEON.Feeder.ApplicationBoard_Copper_Signal_1.gbr, AEON.Feeder.ApplicationBoard_Copper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]
2023-06-01 Update README.md
    Added main file to load to get 3d model assembly in Inventor
